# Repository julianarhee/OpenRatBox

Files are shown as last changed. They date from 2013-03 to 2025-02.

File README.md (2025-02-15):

# Open Rat Box
This repository contains part files and instructions for high-throughput behavior rig towers (current and previous designs).

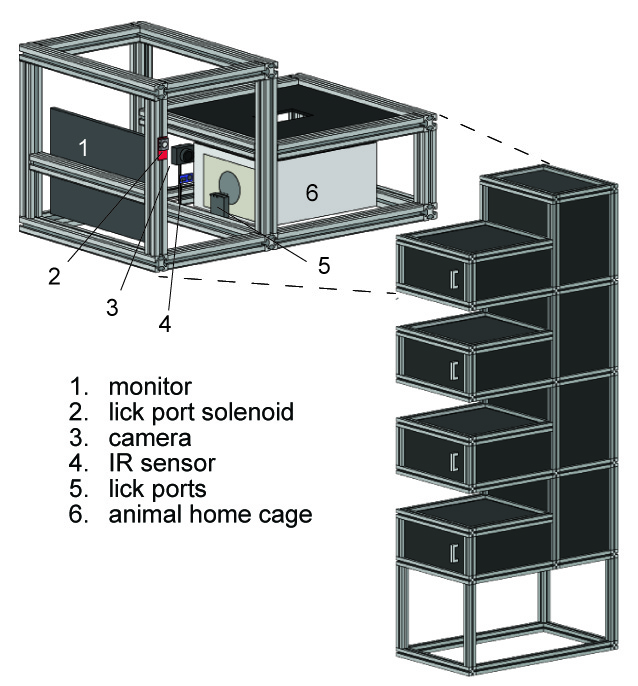
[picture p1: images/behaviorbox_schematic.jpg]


## Components 
- cage: cage info (mounting point dimensions, etc...)
- camera: webcam info
- displays: small computer monitor & optional usb touchscreen display
- frame: 80/20 extrusion bars 
- acrylic panels: structural (walls, ceiling, floor), and useful mounts  
- plumbing: 1/4" ID tubing for connecting water pump to the lick ports (feeding needles attached with luer locks)
- pumps: syringe pumps that can be programmed to deliver set amounts of fluid based on speed, tubing diameter, etc.
- sensors: IR reflector to detect presence/absence of the head poking out of the cage, touch sensors wired to feeding needles (lick ports) to detect lick or no lick

## Instructions
`instructions`: Start here!
- `instructions/behav_rg_special_notes.md`: Contains construction notes and additional tips.
- `instructions/behav_rig_specs_final.xls`: Optional spreadsheet to sort out what size bulk acrylic to buy based on dimensions of custom cut acrylic pieces (disclaimer: might not be fully accurate).

## Design files
`add_ons`: Additional acrylic pieces for the tower.
- `add_ons/cage_hole`: Creates an acrylic hole for the rat's head during training. The `inner_plate` attaches inside the cage and the `outer_plate` mates to it on the outside. Both plates are not necessary if just gluing the plates directly to the cage. Start by drilling or cutting a large hole in the cage, then place the acrylic plate with the (more nicely) laser-cut hold on top to create a smoother opening for the head.
- `add_ons/extrusion_support`: Add these to provide support at the junction connecting two extrusion bars. Use the through holes and M6-slot bolts placed on either side of the connection between the bars.
- `add_ons/power_squid_mount`: Convenient mount to hold up a powerstrip for a given training box. We used a power squid rather than a strip.
- `add_ons/spacers`: For use with repurposed metal frames that hold cages in portable colony racks. These are useful to make the metal rack fit snuggly between the top and bottom panels of the main vestibule.

`displays/usb`: Option mounting piece for attaching a little touchscreen display to control each computer.

`foamboard`: Additional pieces to block out light around the separate front area where the monitor is, in front of the rat and main vestibule (can ignore the foamboard folder in `front_area`)
- `foamboard/rack_top`: captured piece for the top and bottom of the front vestibule that contains the monitor
- `foamboard/front_slim`: Fills the gap above the main vestibule (the "L" shape of the box creates blank space above)
- `foamboard/side_captured`: If not using an acrylic side panel (see `main_vestibule/sides`), can just use a foamboard to close the area on the side.

`front_area`: This is the part of the training box that does not contain the rat cage, but just the monitor, separate from the main vestibule.
- `front_area/monitor_mount`: acrylic panel with through holes for mounting a monitor to the extrusion bar
- `front_area/side_frame`:  Can be used with `side_door` or `side_slotted`. This panel creates a frame whose outer edges are fit into the extrusion rails. It has holes to then attach a door, either via thumbscrew (`side_door`) or fully screwing in at all four courners (`side_slotted`)
- `front_area/side_door`: If using `side_frame`, this is a simple rectangular piece that can be detached/attached with a thumbscrew. Useful for closing off the side, but can be removed (if using oe of the frame pieces) to access wires and such on the monitor-side of the vestibule.
- `front_area/side_slotted`: Screws into `side_frame` with 4 screws, and has a small slotted opening for wires to come through

`main_vestibule`: Where the rat cage is
- `base`: bottom or floor of the vestibule
- `door`: door that attached with hinges and has a handle to make it easy to open/close the box
- `lid`: top of vestibule
- `sides`: sides of vestibule (they should be oriented the same way)
- `front_clear`: `frame` fits into the extrusion rails, and is meant to make the `attachment` window pane removable. The `attachment` panel screws into the `frame` in 4 corners, and also contains slotted holes to allow wiring from the lick ports to come through, out of the front vestibule.

`sensors`: Mounts to hold various sensors
- `head`: If using an IR reflector sensor to detect head presence/absence, holds that phidget sensor in place. Not really critical, as the small PCB can be directly screwed onto the MicroRax frame that sits between the `main_vestibule/front_clear` panel and the rat's cage hole.
- `lick`: 1 or 3 lick ports (clear). Holds the feeding needles that deliver reward, which are also metal (conductive). A small hole should be tapped at the top (M2.5) to hold the lick spout in place, like a set screw. A flat washer can be placed under the screwhead with a wire soldered on in order to create a connection between the lick port and the little touch sensor board outside of the vestibule.
- `phidget_mounts`: A mount to hold the USB-phidget which connects all the different sensor boards (IR reflector, touch sensors for the lick port detection, etc.)

`tower_frame`: All specifications for the custom-cut extrusion bars, and additional notes.

`x_everything`: When in doubt, all the pieces (might not contain everything though). Always use the most recent version.

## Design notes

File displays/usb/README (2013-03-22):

To setup the usb display...

1) install display driver: http://www.displaylink.com/support/mac_downloads.php
2) install touch driver: http://www.touch-base.com/documentation/mimotouchdevice.htm
3) calibrate
4) set as primary display

Notes
------

After proper installation, should have "UPDD Console" and "UPDD Calibrate" programs. Use the Console to choose Display 1 as the touchscreen monitor (primary), then calibrate by clicking correct icon in the Console (use precise pointer to touch the 4 calibration points).

The display driver may not work with 'Standard' rotation of the display. If so, set the rotation to 180, and flip the monitor. Then recalibrate the touch screen.

Additional configuration information: http://www.mimomonitors.com/pages/mac-os-x-install-procedures-for-mimo-710-710-s-720-s-740

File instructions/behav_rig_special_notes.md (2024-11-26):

# Building notes
- Do not build the entire tower out of the anodized extrusion bars first. Start with the base, then build each unit on top of the next. 
- Use the labeled tower diagram to make sure bars are not mixed up (components A, B, C, etc. in `tower_frame/rat_box_assembly.png`). Each component has its own specification, such as which ends are tapped, which are not, etc. 
- Read the whole document (especially "Idiosyncracies for construction"). 
- Laser-cut and prepare all custom modifications for a *single* unit (the bottom unit) first. Only once you are satisfied with the base unit, then can cut more pieces for each unit. 

## Custom components
- All laser-cut pieces
- MicroRax frame & attachment pieces (LED, camera, sensors) for all components near the head and lickport area inside the main vestibule
- wiring: LEDs (IR for camera, etc.), phidget sensors (IR reflective sensor for head-detection & to lick spouts)
- tubing: helpful to have an extra, long piece of tubing to attach to the lick ports when flushing the system for cleaning. Supergluing a small rubber black O-ring to the cross-section of tube will help create a snug fit onto the rounded lickport spout

## Modifications related to laser-cut parts

### Pieces that need tapped holes
- `lickHolder`: needs 2 tapped holes for M2.5 screws
- `frontPanelFrame` (clear):  needs 4 tapped holes for M3 screws (tap M3x0.50)
-side door frame (black, captured):  needs 1 tapped hole at the top if using thumb-screw for panel

### Pieces with added holes
- `monitorMount` ("big"): make spacing of 4 through holes match whatever mount the monitor needs\
- `touch_sensor_panel` (for `phidget_mounts`): drill little holes above each sensor board for zip-ties to hold soldered wires straight up (prevents bending)

### Bulk acrylic order adjustments
- Make sure large, bulk pieces fit the laserbed, for ex., cut in half (18.5" and 17.5", not 36") to fit
- `phidget_mount` and `touch_sensor_panel` (clear): cut with 1/8" acrylic (not 1/4")
- might need more black 1/4" for `side_door_frame` depending on size (capture inside extrusion rivets)
- `cage_head_thruHole` (for gluing to front of rat cage where head pokes out): use 1/8" rather than 1/4" acrylic for spacing

## Idiosyncracies for construction:
1. If using spring-loaded spacer pieces (which can also be used for optional air flow) should be installed *before* putting in the lid/bottom panels. These pieces go on the underside of the top frame of the vestibule, so it is easier to screw them on (springs, screws, etc.) when the panel is upside down than when installed.
2. If using repurposed metal brackets from the colony cage system, for a snug fit, helpful to add: one 1/4" acyrlic spacer set on bottom (use M5x20s), and two stacked 1/4" spacers attached to top/lid piece (use M5x25s).
3. All vertically-oriented extrusion pieces should be screwed in to its lower horizontal piece before stacking the next unit on top of rack. Otherwise, you cannot access the end-fastener at the bottom of the vertical piece once it is in place.
4. `main_vestibule/lid/Lid` and `base/Bottom`: These are the black acrylic panels that are fitted into the extrusion frames forming the top (lid) and floor (bottom) of the main vestibule holding the plastic rat cages. The etched text (in the laser cut pattern) should be facing up. And, "insert this side first" means that end goes toward the monitor first.
5. `main_vestibule/sides/sidePanel_final_rot`: Side panels for main vestibule should face the same direction, so the text should be facing leftward, if facing the monitor.
6. `main_vestibule/front_clear/frame` and `front_clear/attachment` pieces  are clear acrylic panels that should be screwed together before inserting (i.e., don't just put the frame in alone while building up the extrusion pieces around it without screwing on the attachment piece, too)

### Helpful ordering of main vestibule:  
(a) Get bottom extrusion frame (3 pieces, sides and front), but without the front piece connected yet, and slide in the acrylic bottom panel. The spacers & metal cage frame should be screwed in already (Note 2 above).
(b) Approximately align the top horizontal extrusion pieces (into which the lid panel will fit) with the horizontal extrusion piece that is  resting above the clear acrylic front panel/attachment
(c) Then, slide in the side panels.
(d) Separately, build up the door (bottom and side extrusion bars, but without the top bar connected). Connect this partial door to the extrusions making up the bottom of the vestibule. Make sure that the side acrylic panels are fitting into the vertical extrusion bars of the door as you screw the door into the end fasteners on the bottom frame's extrusion bars.
(e) With the top extrusion bar of the door still off, slide in top acrylic panel for the lid. Then, slide in the extrusion bar that will connect the edge closest to the door of the top panel and the top of the door.

### Some more notes:
- For securing the top/bottom acrylic panels, manuever the pieces so that for each panel, 3 edges (two sides and the edge closer to the monitor) are resting on the extrusions that make up the sides and front (closest to monitor) of the vestibule. Place the 4 panel pieces (sides, top, bottom) in the approximate places, and don't tighten until things are well in place. Make sure all panels are securely backed all the way in (toward the monitor), i.e., the acrylic panels should nestle fully into the rails of the extrusion bars.
- Make sure clear acrylic front panel attachment is screwed onto the front panel frame when inserting into extrusions during building (extrusions on top of the frame were sitting too low, so the front panel attachment did not fit.  had to shave off a little bit off the top of the attachment piece)\
- Add support extrusions to bottom carriage to provide extra support across the longer axis (rigs may bend forward otherwise). Use 2 M6 T-slot nuts, with acrylic piece, same length as 4 main carriage extrusion pieces.

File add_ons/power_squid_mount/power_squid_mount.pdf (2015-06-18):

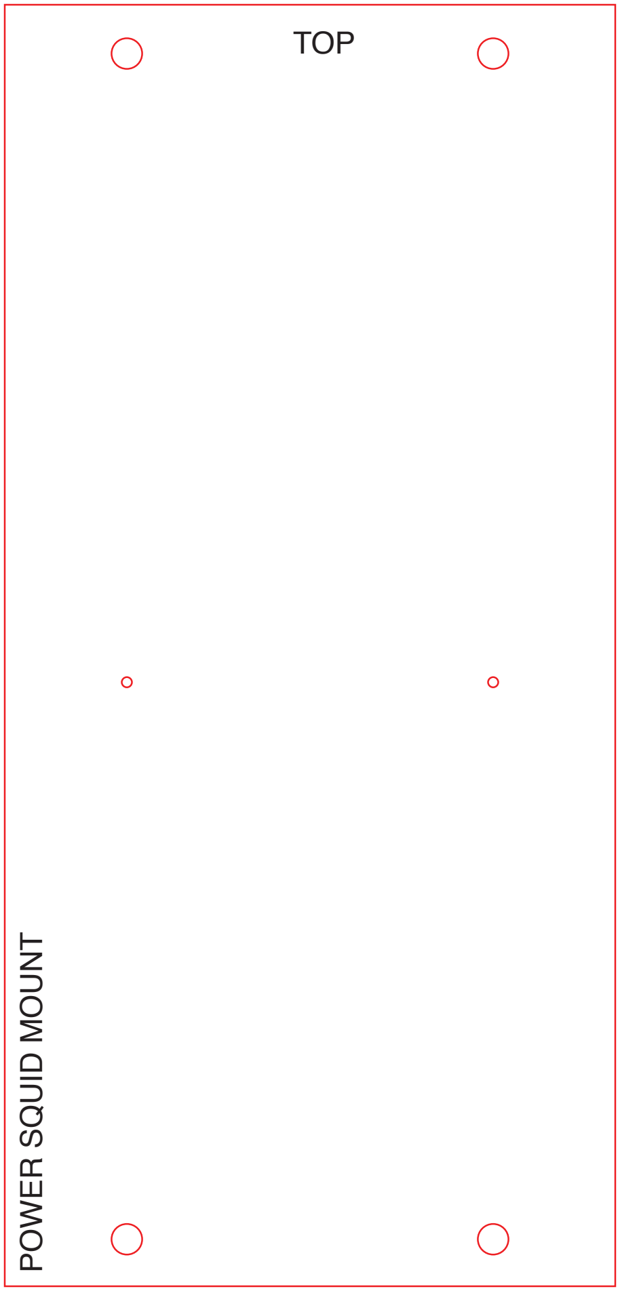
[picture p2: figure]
TOP; POWER SQUID MOUNT

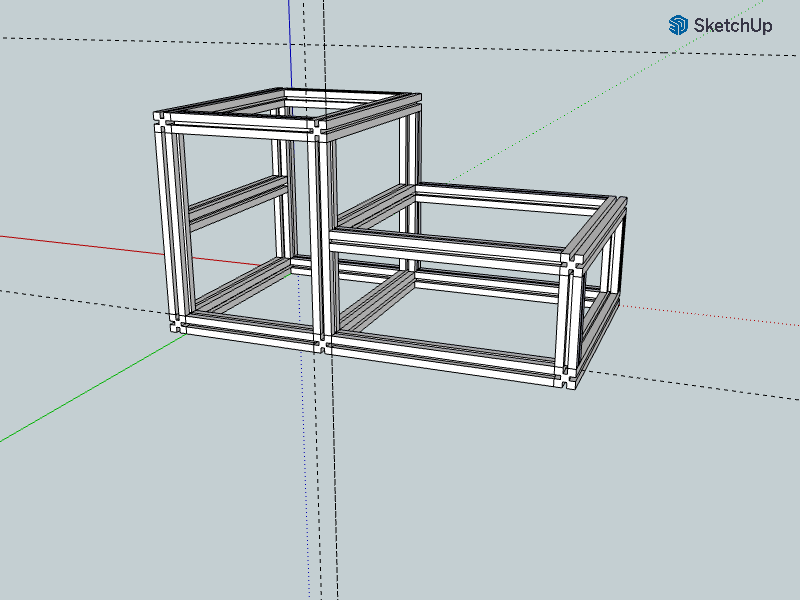
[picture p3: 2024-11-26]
tower_frame/rat_box.png

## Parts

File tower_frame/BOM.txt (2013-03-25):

All pieces below: 4040-lite, black anodized

Per Box (4 per tower):

4x  A	(525mm, end fastener access holes, both sides, both axes)
	40-4040-LITE X 525MM
	80/20 Metric Extrusion
	Black Anodized.With 40-7050 Style MA in R&S Left End and 40-7050 in R&S Right End.
	
2x  B	(210mm, both sides tapped for end fasteners)
	40-4040-LITE X 210MM
	80/20 Metric Extrusion
	Black Anodized. With 40-7059 Both Ends

4x  C	(450mm, tapped on one side for e.f., milled on other for anchors)
	40-4040-LITE X 450MM
	80/20 Metric Extrusion
	Black Anodized. With 40-7059 One End,& 40-7044 @ A,C Opposite End.

2x  D	(445mm, milled for anchor fasteners on both sides, same axis -- e.g. A&C)
	40-4040-LITE X 445MM
	80/20 Metric Extrusion
	Black Anodized. With 40-7044 @ A,C Both Ends.

2x  E 	(300mm, tapped on both sides for e.f.)
	40-4040-LITE X 300MM
	80/20 Metric Extrusion
	Black Anodized. With 40-7059 Both Ends.

4x  F 	(385mm, tapped on one side, milled for a.f. on other)
	40-4040-LITE X 385MM
	80/20 Metric Extrusion
	Black Anodized. With 40-7059 One End & 40-7044 @ A,C Opposite End.

Capping off the top (1 per tower)

2x A
2x E

Bottom carriage (1 per tower)

6x  G   (280mm, tapped on one side, milled for a.f. on other)
	40-4040-LITE X 280MM
	80/20 Metric Extrusion
	Black Anodized. With 40-7059 One End & 40-7044 @ A,C Opposite End.

2x  H 	(790mm, tapped on both sides for end fastener)
	40-4040-LITE X 790MM
	80/20 Metric Extrusion
	Black Anodized. With 40-7059 both Ends.

+2x A

Full tower:

A: (4*4) + 2 + 2 = 20
B: (2*4) = 8
C: (4*4) = 16
D: (2*4) = 8
E: (2*4) + 2 = 10
F: (4*4) = 16
G: 6
H: 2

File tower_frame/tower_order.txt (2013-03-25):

2 Towers:

A: ((4*4) + 2 + 2) * 2 = 40
B: (2*4) * 2 = 16
C: (4*4) * 2 = 32
D: (2*4) * 2 = 16
E: ((2*4) + 2) * 2 = 20
F: (4*4) * 2 = 32
G: 6 * 2 = 12
H: 2 * 2 = 4

(less extra from past orders + 2 for safety margin)
A: 40 - 12 + 2 = 30
B: 16 + 2 = 18
C: 32 + 2 = 34
D: 16 + 2 = 18
E: 20 - 12 + 2 = 10
F: 32 + 2 = 34
G: 12 + 2 = 14
H: 4 + 2 = 6

30x  A	(525mm, end fastener access holes, both sides, both axes)
	40-4040-LITE X 525MM
	80/20 Metric Extrusion
	Black Anodized.With 40-7050 Style MA in R&S Left End and 40-7050 in R&S Right End.	
18x  B	(210mm, both sides tapped for end fasteners)
	40-4040-LITE X 210MM
	80/20 Metric Extrusion
	Black Anodized. With 40-7059 Both Ends

34x  C	(450mm, tapped on one side for e.f., milled on other for anchors)
	40-4040-LITE X 450MM
	80/20 Metric Extrusion
	Black Anodized. With 40-7059 One End,& 40-7044 @ A,C Opposite End.

18x  D	(445mm, milled for anchor fasteners on both sides, same axis -- e.g. A&C)
	40-4040-LITE X 445MM
	80/20 Metric Extrusion
	Black Anodized. With 40-7044 @ A,C Both Ends.

10x  E 	(300mm, tapped on both sides for e.f.)
	40-4040-LITE X 300MM
	80/20 Metric Extrusion
	Black Anodized. With 40-7059 Both Ends.

34x  F 	(385mm, tapped on one side, milled for a.f. on other)
	40-4040-LITE X 385MM
	80/20 Metric Extrusion
	Black Anodized. With 40-7059 One End & 40-7044 @ A,C Opposite End.

14x  G   (280mm, tapped on one side, milled for a.f. on other)
	40-4040-LITE X 280MM
	80/20 Metric Extrusion
	Black Anodized. With 40-7059 One End & 40-7044 @ A,C Opposite End.

6x  H 	(790mm, tapped on both sides for end fastener)
	40-4040-LITE X 790MM
	80/20 Metric Extrusion
	Black Anodized. With 40-7059 both Ends.

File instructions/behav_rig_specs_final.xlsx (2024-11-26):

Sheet: acrylic piece sizes to order
Piece | File Name | Material | Width | Height | Bulk Piece Assignments: |  |  | laserbed | base or lid | door |  | sensor base (2) |  | TOTAL:
Base | Bottom_v6 | Acrylic (1/4") | 18 | 18.5 |  | c | b1 | W: | 18.5 | 17.25 |  | 8 |  | 35.75
Lid | Lid_v11 | Acrylic (1/4") | 18 | 18.5 |  | c | b1 | H: | 18 | 8.825 |  | 1 |  | 9.825
Door | door_v6 | Acrylic (1/4") | 17.25 | 8.825 |  | c | b3
door hinge | doorHinge_v8 | Acrylic (1/4") | 4 | 8.24 |  | c | b3 | laserbed | lid | spacers | monitor mount | door hinge | 1 cage head hole | 3 sensor bases | 9 lick holders | TOTAL:
lick spout holder | lickHolder_v4 | Acrylic (1/4") | 0.663 | 1.5 |  | c | b3 | W: | 18.5 | 9 | 8.5 | 8.25 | 5 | 3 | 9 | 36 | 35.75 | 35.5 | 35.5
Monitor mount | monitorMount_v3 | Acrylic (1/4") | 8.5 | 6 |  | c | b3 | H: | 18 | 15 | 6 | 4 | 8 | 8 | 1.5 | 18 | 16.5 | 18
sensor base | sensorBase_v? | Acrylic (1/4") | 8?? | 1 | *check, bec IR distance is 10cm, or approx 4in. | c | b3
side panel | sidePanel_v2 | Acrylic (1/4") | 18.5 | 8.852 | (x2) | c | b1 |  | 8.5 | 27.5
spacer (air) | spoutSpacer_v1_airOnly1c | Acrylic (1/4") | 5 | 4.5 | (x3) | c | b2
spacer (H2O) | spoutSpacer_v1_H2Oonly | Acrylic (1/4") | 5 | 4.5 | (x3) | c | b2
(cage head hole pieces) |  | Acrylic? | 8 | 5 | (x2) |  | b3 | Estimated Bulk Acrylic Pieces to Order:
 |  |  |  |  |  |  |  | b1 | 18x18.5 | 3
front panel frame | frontPanelFrame_v2 | clear Acrylic | 18.4 | 8.852 | *inner area = 16.5x6.85 |  |  | b2 | 9x15 | 1
front panel | frontPanelAttachment_v2 | clear Acrylic | 17.37 | 8 |  |  |  | b3 | 18x19 | 1
phidget sensor holder | x | clear Acrylic | 7.5 | 4.5
phidget holder | x | clear Acrylic | 7.5 | 3.5 |  |  |  |  |  |  |  | 25
 |  |  |  |  |  |  |  | c1 | 9x36 | 1
monitor side cover (removable) | x | Foam board | 15 | 18 | f3
monitor side cover (trapped) | use monitorFloor_v2 (w/o slots) | Foam board | 18.5 | 12.5 | f2
Monitor area base | monitorFloor_v2 | Foam board | 18.5 | 12.5 | f2 |  |  | 36 | 17 |  |  | 6
back monitor cover top | use sidePanel_v2 (w/o corners) | Foam board | 18.5 | 8.852 | f1 |  |  | 15 | 25.5
back monitor cover (bottom) | use sidePanel_v2 (add slots) | Foam board | 18.5 | 8.852 | f1
front cover panel | x | Foam board | 18.5 | 6.5, 6.25 | f4 |  |  | Estimated Bulk Acrylic Pieces to Order:
top cover panel | x | Foam board | 18.5 | 13 | f2 |  |  | f1 | 18x18.5 | 1
 |  |  |  |  |  |  |  | f2 | 18x13 | 3 | 17
 |  |  |  |  |  |  |  | f3 | 18x15 | 1
 |  |  |  |  |  |  |  | f4 | 18.5x7 | 1
 |  |  |  | 33.5 | 13 | 37
 |  |  |  | 31.5 | 25.5

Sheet: accessory pieces
MAIN VESTIBULE:
1. LID AND BASE
Set Panel Holder (M8x16mm) | 8x | (top and bottom panels each req. 4)
1a. Base piece
M5x20 w/ M5 nuts + flat/lock washers | 6x | (attach frame and 1 set of spout spacers to bottom panel)
M5x10 w/ M5 nuts + lock washers | 6x | (to connect metal frame to L-bracket -- aligns elongated hole of L-bracket)
L-brackets (M5 hole & elongated hole) | 12x | (for spout spacers)
1b. Lid piece
M5x25 w/ M5 nuts + flat washers | 6x | (for 2 sets of spout spacers to lid)
(cone springs) | 2x | (come with old rack)
(half-threaded screws for plastic vents) | 6x | (come with old rack)
(pastic vents) | 2x | (come with old rack)
M4x10 (flat, phillips head -- flush with frame) | 4x | (for mac mini cuff -- comes with mac cuff)
Mac Mini cuff | 1x
2. Door
M6x16, + M6 nut; flat-lock washers | 2x | (for attaching door_hinge panel to hinge)
Hinge | 1x | (comes with 4 M6 roll-in T-slot nuts & M6 screws: use 2 to attach hinge to extrusion, \
 |  |  | other 2 go on opposite extrusion bar, to attach slim piece for dead-bolt)
M6x25, + M6 nut; flat--flat-lock washers | 2x | (for attaching door_main to door_hinge panel)
Dead bolt | 1x
M5x12, + M5 nut; flat-lock washers | 4x | (for attaching dead-bolt to acrylic door_main piece)
Door handle | 1x
M4x10, + flat washers | 2x
(M6 w. roll-in T-slot nut) | 2x | (for attaching hinge to Extrusion; comes with Hinge)
(M6 w. roll-in T-slot nut (for dead bolt) | 2x | (for dead-bolt latch to attach to extrusion; comes with Hinge)
3. Front clear panel piece
M3x10 | 4x | (front clear panel -- screw into tapped holes on front_panel_frame piece, captured)
MONITOR AREA:
1. Monitor
M4x20 (or M4x25) screws | 4x | (for screwing back of monitor to monitor_mount)
Large flat washers (M4) | 4x
M6 w/ roll-in T-slot nut | 2x | (for attaching monitor_mount to extrusion bar)
2. Side door
M6 thumb screw | 1x | (for screwing side door onto side_door_frame, captured -- tapped hole)
(black vinyl cover, as a "window curtain"?)
... door should just be red acrylic?? (1/8")
Wheels
M6(or M8) w/ roll-in T-slot nut | 12x
wheels | 4x
SENSORS
1. Phidget / attachments
M6 w. roll-in T-slot nut | 4x | (attach phidget and touch-sensor mounts)
M4x16 w/ (rectangular) drop-in nut (+ M4 flat washers, for pumps) | 2x; 2-4x | (Startech network adaptor; 1-2 pumps) -- roll-in spring loaded ones might be better, esp for pumps…
Touch Sensors | 1-3x
IR Reflective sensor (min 10 cm) | 1x
USB camera (Newegg) | 1x
red LED light bar | 1x | (+ power source for 4 LEDs -- per tower)
Reward spouts | 1-3x
M2.5 x6mm (with washers, flat and lock) | 2-6x | (for each spout)
wire w/ banana clips & U-hooks | 3x | (to connect each spout to phidget sensor)
(sheet metal piece) | 1-3x | (for each spout)
2. MicroRax Parts
320 cm bar (350 cm might be fine, too) | 1x
M3x6 (connects 90deg bracket to L-bracket & microrax frame) | 2x | <-- if get correct length long-bar, might not need
M3x5 (reg head) for all else
M3x5 low-head -- for 90deg bracket between 2cm & 4cm piece (holds lick-spout piece) | 2x, w/ lock washers
M2.5x6 (for holding spout) | 2x
M3x8 (for holding lick-spout acrylic piece to frame) | 2x
cage-frame mount bar, 160 cm
head-sensor bar, 140 cm
spacer bar (attaches to truss piece), 4cm (or 5cm)
camera stand, 6cm (attaches to cage-frame mount bar)
lick-spout bar, 4cm
OLD microrax arrangement for sensors:
200mm bar | 2x | MicroRax frame
300mm bar | 2x | MicroRax frame
M3 (like MicroRax kit screws and T-slot/reg nuts) | (22x, nut bar; 4x, reg nut) | (to make MicroRax frame)
M3(x16) with washers | min 2x | (for MicroRax frame to base)
2mm bar pieces
4mm bar pieces
flat L-brackets (to connect frame pieces) | 4x + however many for add-on pieces
short 90-deg brackets + screws/nuts | ? X | (plus, 1 M3x8 (?) for connecting 90-deg bracket + (washer) + nut-plate on frame)

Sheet: finalized pieces
Piece | File Name | Material | Width | Height | Qty/setup: | Qty/rack: | Raw Piece: | Price | laserbed | base or lid | door |  | sensor base (2) |  | TOTAL:
MAIN_VESTIBULE
Base | Bottom_v5_imported_rot_text_dxf.dxf | black Acrylic (1/4") | 18 | 18.5 | 1x | 4x | B1, 1x |  | W: | 18.5 | 17.25 |  | 8 |  | 35.75
Lid | Lid_v15_imported_rot_text_dxf.dxf | black Acrylic (1/4") | 18 | 18.5 | 1x | 4x | B1, 1x |  | H: | 18 | 8.825 |  | 1 |  | 9.825
Door (main) | door_final_text.dxf | black Acrylic (1/4") | 17.25 | 8.825 | 1x | 4x | B3
Door (hinge) | doorHinge_final_rot.dxf | black Acrylic (1/4") | 4 | 8.24 | 1x | 4x | B4*, use inner area -- makes 2x per B4 piece) |  | laserbed | lid | spacers | monitor mount | door hinge | 1 cage head hole | 3 sensor bases | 9 lick holders |  | TOTAL:
Front Panel (attachment) | frontPanelAttachment_final_rot.dxf | clear Acrylic (1/4") | 17.37 | 8 | 1x | 4x | C1a (17.5"x9")
Front Panel Frame (tapped, M3, x4) | frontPanelFrame_final_rot.dxf | clear Acrylic (1/4") | 18.4 | 8.852 | 1x | 4x | C1b (18.5"x9"), *inner area = 16.5x6.85
sides (2x) | sidePanel_final_rot_text.dxf | black Acrylic (1/4") | 18.5 | 8.852 | 2x | 8x | B1, 1x
 |  |  | (tot: 18.5 x 18")
FRONT VESTIBULE (Monitor) | [sideDoorAttachment_v4 is the shorter panel -- use this]
side door (attachment) (M6 thumb or 4 M3 tapped) | sideDoorAttachment_v5_imported_dxf.dxf | black Acrylic (1/8") | 11.5 | *15 (short version) | 1x | 4x | r1* (12x16), 1x -- GET IN CLEAR-RED ACRYLIC, 1/8" if possible
side door (frame) (tapped, M6, x1) | sideDoorFrame_v4_imported_dxf.dxf | black Acrylic (1/4") | 12.5 | 16.25 | 2x | 8x | B4* (12.5" x 16.5"), *inner area = 10x13"
Monitor mount | monitorMount_final_rot.dxf | black Acrylic (1/4") | 8.5 | 6 | 1x | 4x | **use B2 sizing -- makes 2x per B2 piece |  | W: | 18.5 | 9 | 8.5 | 8.25 | 5 | 3 | 9 |  | 36 | 35.75 | 35.5 | 35.5
(monitor mount, "big") | (curr: monitorMount_v3_big.dxf -- spacing off) | black Acrylic (1/4") | 8.5 | 6 | (1x) | (4x) | " " |  | H: | 18 | 15 | 6 | 4 | 8 | 8 | 1.5 |  | 18 | 16.5 | 18
**side_door_slotted (4 M3 tapped) | (curr: side_door_slotted_v1 -- make slot smaller) | black Acrylic (1/8") | 11.5 | 15 | 1x | 4x | b1*, 1x
FOAMBOARD PIECES
front slim (captured) | frontSlimCaptured_v2_imported_rot.dxf | Foam board | 18 | 6 | 1x | 4x
*monitor floor | (use same piece as rackTop) | Foam board | 18.5 | 12.5 | 1x | 4x
*rack top | rackTop_final_imp.dxf | Foam board | 18.5 | 12.5 | n/a | 1x
ADD-ONS
(spacer, air only) | spoutSpacer_airOnly_final_imported_rot_text.dxf | black Acrylic (1/4") | 5 | 4.5 | (3x) | n/a | n/a
(spacer, H2O) | spoutSpacer_H2Oonly_final_imported_text.dxf | black Acrylic (1/4") | 5 | 4.5 | (3x) | n/a | n/a |  |  | 8.5 | 27.5
spacers (all, for 9"x15" piece): | spoutspacers_all_imported.dxf | black Acrylic (1/4") | 9 | 15 | 1x | 4x | B2, 1x
cage head hole pieces - inner (tapped, M3/4?, x4) | cage_head_tapHole_imported_dxf.dxf | black Acrylic (1/4") | 8 | 5 | 1x | (4x) | B4*, use inner area -- makes 3x per B4 piece
cage head hole pieces - outer (thru) | cage_head_thruHole_imported_dxf.dxf | black Acrylic (1/8") | 8 | 5 | 1x | 4x | b1* (2 per b1 piece)
extrusion supports | extrusionSupport_imported_dxf.dxf | black Acrylic (1/4") | 1.5 | 4 | n/a | 4x | (can use scrap pieces)
 |  |  |  |  |  |  |  |  | B1 | 18x18.5 | 3 | .=>
touch sensor holder | touch_sensor_panel.pdf | clear Acrylic (1/8") | 7.5 | 4.5 | 1x | 4x | ** |  | B2 | 9x17.5 | 1
phidget holder | touch_sensor_panel.pdf | clear Acrylic (1/8") | 7.5 | 3.5 | 1x | 4x | ** |  | B3 | 18x19 | 1 | NO
lick spout holder (tapped, M2.5, x2) | lickHolder_v6_imported_dxf (1).dxf | clear Acrylic (1/4") | 1.6 | 1 | 1x - 3x | 4x - 12x | C1b (make out of inner area of front frame) |  | B4 (new) | 12.5" x 16.5" | 2
[head sensor holder ] | mag_head_sensor.pdf | black Acrylic (1/4") | 1.25 | 1.25 | 1x | 4x+ | (scrap pieces, not part of new design) |  |  |  |  |  |  | Per Setup | Per Tower
 |  | black Acrylic (1/8") | 1.25 | 1.25 |  |  | " " |  | B2' | 9x15 | 1 | (2 monitor_mounts) |  | 0.5x | 2x
 |  |  |  |  |  |  |  |  | **adjust to 9" x 17.5" -- use B2to make door (dims 17.25x8.825), getting rid of "B3" piece, plus giving extra 2.5" pieces for scraps
 |  |  |  |  |  |  |  |  | B2 adjusted | 9x17.5 | 1 | (1 door) |  | 1x | 1x
RAW ACRYLIC TO ORDER:
black 1/4" acrylic (18.5"x18") |  |  |  |  |  |  |  |  | C1 | 9x36 | 1
black 1/4" acrylic (19"x18") |  |  |  |  |  |  |  |  | **splt C1 original to: |  | (a) 9" x 17.5" |  | "C1" (=C1a) | 1x | 4x
black 1/4" acrylic (15"x9") |  |  |  |  |  |  |  |  |  |  | (b) 9" x 18.5" |  | "C2" (=C1b) | 1x | 4x
clear 1/4" acrylic (17.5"x9") |  |  |  |  |  |  |  |  | b1 | 12" x 16" | 1 |  | "b1" | 1x | 4x
clear 1/4" acrylic (18.5"x9") |  |  |  |  |  |  |  |  | c1 | (have)
black 1/8" acrylic (W" x H")
clear 1/8" acrylic (W" x H")
black foamboard |  |  |  |  |  |  | RAW ID: | DIM: | PIECE | PER SETUP | PER TOWER | Total: |  | 2 TOWERS: | Already Have: | Need: | NEW ORDER (04.10.2013) |  | *needed amount + 4 extra of each piece (except black 1/8")
black vinyl |  |  |  |  |  |  | B1 | black 1/4" acrylic (19"x18") | "B1" | 3x | 12x | 12 |  | 24 | -28 | 0 | 4
 |  |  |  |  |  |  | B2 | black 1/4" acrylic (17.5"x9") | "B2" | 2x | 8x+2x(B2') | 10 |  | 20 | -8 | 12 | 16 | *changed | [for 8 doors, 8 monitor mounts]
 |  |  |  |  |  |  | B4 | black 1/4" acrylic (12.5"x16.5") | "B4" | 2x | 8x | 8 |  | 16 | 0 | 16 | 20 (sheet makes 24) | *new | [for 16 side_door_frames]
**03.11.2013 notes: |  |  |  |  |  |  | C1 | clear 1/4" acrylic (17.5"x9") | C1 | 1x | 4x | 4 |  | 9 | -9 |  | 4
(1). Change CLEAR acrlyic general dimensions (to fit laser bed) -- also, remove "phidget sensor mount" pieces |  |  |  |  |  |  | C2 | clear 1/4" acrylic (18.5"x9") | C2 | 1x | 4x | 4 |  | 9 | -9 |  | 4
(2). Add 1/8" acrylic pieces -- phidget sensor mounts (both--phidget mount, and lick-sensor mount)
(3). Remove monitor-back covers -- these will just be vynl pieces (add this!), along witih magnetic strips OR just gaffer's tape |  |  |  |  |  |  | b1 | black 1/8" acrylic (12"x15") | b1 | 1x | 4x | 4 |  | 8 | -7 | 9 | 9 | [1 more, plus 8 extra, in case replaced]
(4). Fix "file names" for each piece! |  |  |  |  |  |  | r1 | clear-red 1/8" acrylic (12"x15") | "r1" | " " | " " | " " |  | " " | 0 | 8 | 20 | *new [get 8, OR get 16, if replace all]
(5). Mark "special instructions" if really important, and also, mark which accessory-pieces go with it… (see tab)
 |  |  |  |  |  |  |  | clear 1/8" acrylic | c1 | (have) |  | 36 x 8 ft | 24 pieces | 48 | 4 setups
*(6). Make (new) "raw" pieces that include several parts in one acrylic piece-to-order |  |  |  |  |  |  |  |  |  |  |  | 48" | 48 x 96 | 60 | 4 setups
(for ex., "acrylic_b3"; include "extrusion support" piece, dwg/dxf) |  |  |  |  |  |  |  |  |  |  |  |  |  | 36 | 3 setups

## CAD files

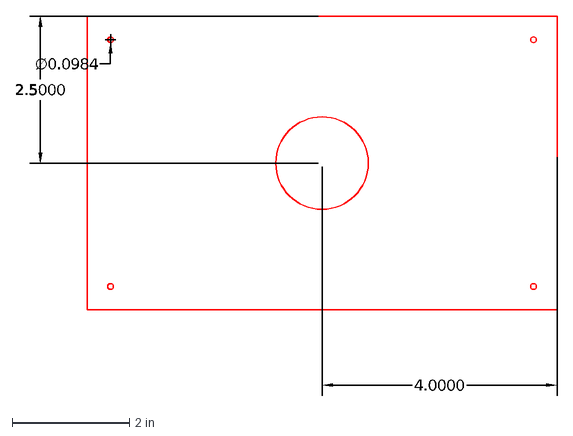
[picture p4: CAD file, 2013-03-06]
add_ons/cage_hole/inner_plate/cage_head_tapHole.dxf
4.0000
2.5000
∅0.0984

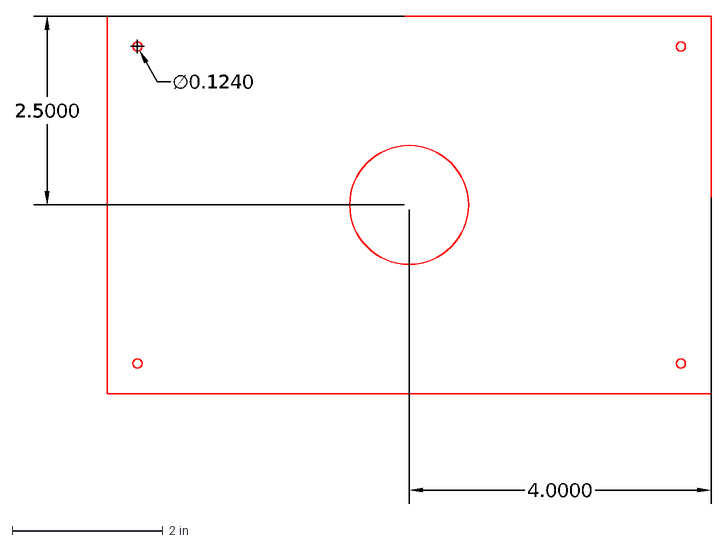
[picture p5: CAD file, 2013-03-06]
add_ons/cage_hole/outer_plate/cage_head_thruHole.dxf
4.0000
2.5000
∅0.1240

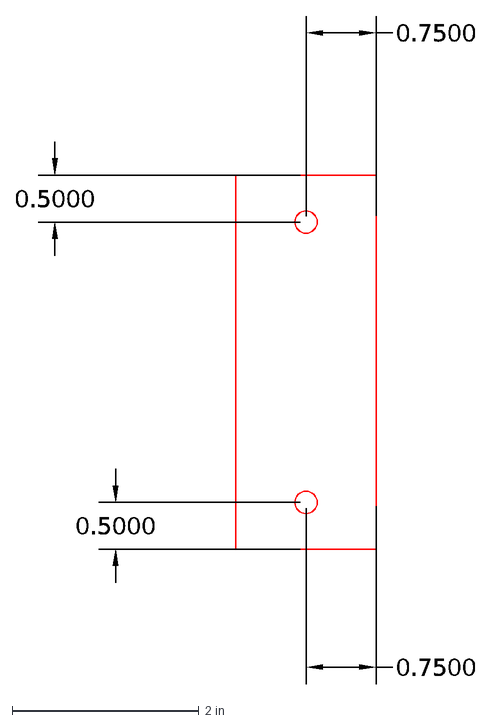
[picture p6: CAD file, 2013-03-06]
add_ons/extrusion_support/extrusionSupport.dxf
0.7500
0.5000

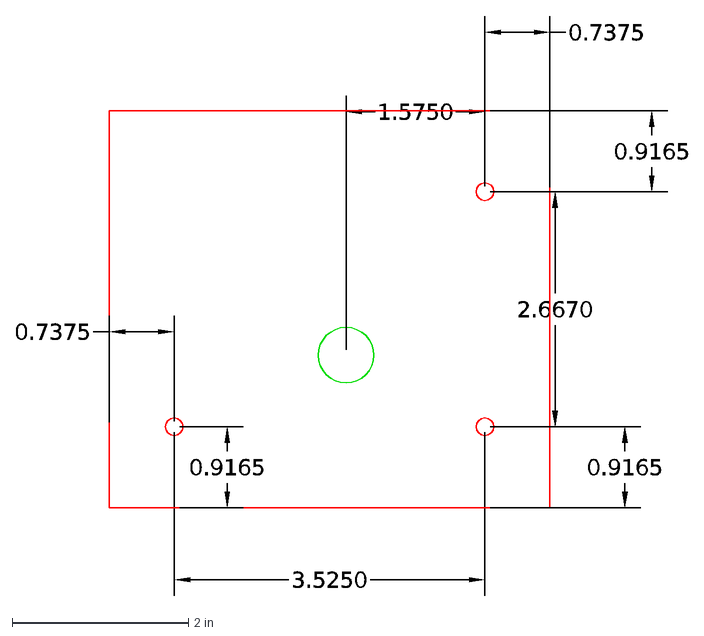
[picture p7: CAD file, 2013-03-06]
add_ons/spacers/singles/spoutSpacer_H2Oonly_final.dxf
2.6670
1.5750
3.5250
0.9165
0.7375

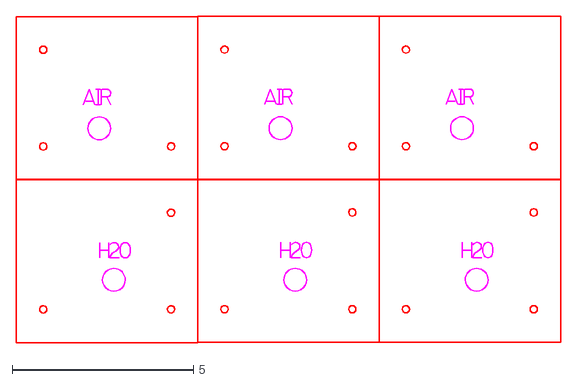
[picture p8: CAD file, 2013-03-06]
add_ons/spacers/spoutspacers_all_imported.dxf
15.0 x 9.00

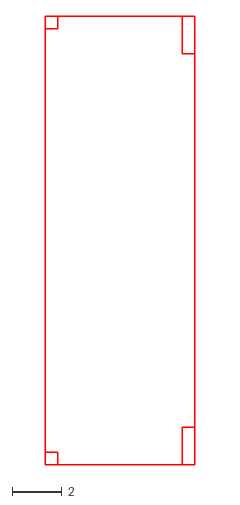
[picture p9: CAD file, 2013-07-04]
foamboard/front_slim/frontSlimCaptured_v4_imported_rot_dxf.dxf
6.00 x 18.0

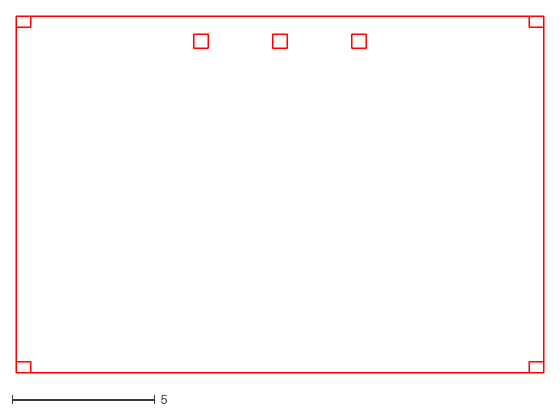
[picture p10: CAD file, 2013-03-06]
foamboard/monitor_floor/monitorFloor_imported_rot_dxf.dxf
18.5 x 12.5

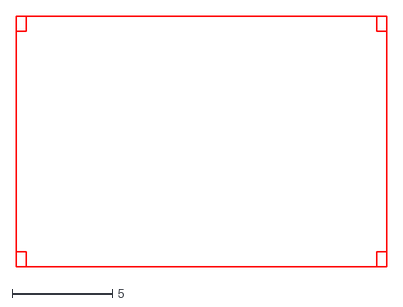
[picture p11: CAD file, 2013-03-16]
foamboard/rack_top/rackTop_final_imported_rot.dxf
18.5 x 12.5

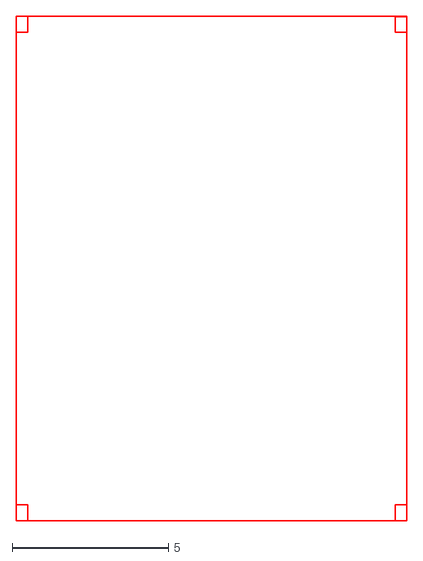
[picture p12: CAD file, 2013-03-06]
foamboard/side_captured/sideCaptured_final_imp.dxf
12.5 x 16.1

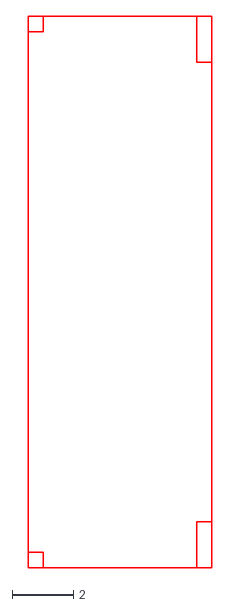
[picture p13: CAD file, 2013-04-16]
front_area/foamboard/front_slim/frontSlimCaptured_v4_imported_rot_dxf.dxf
6.00 x 18.0

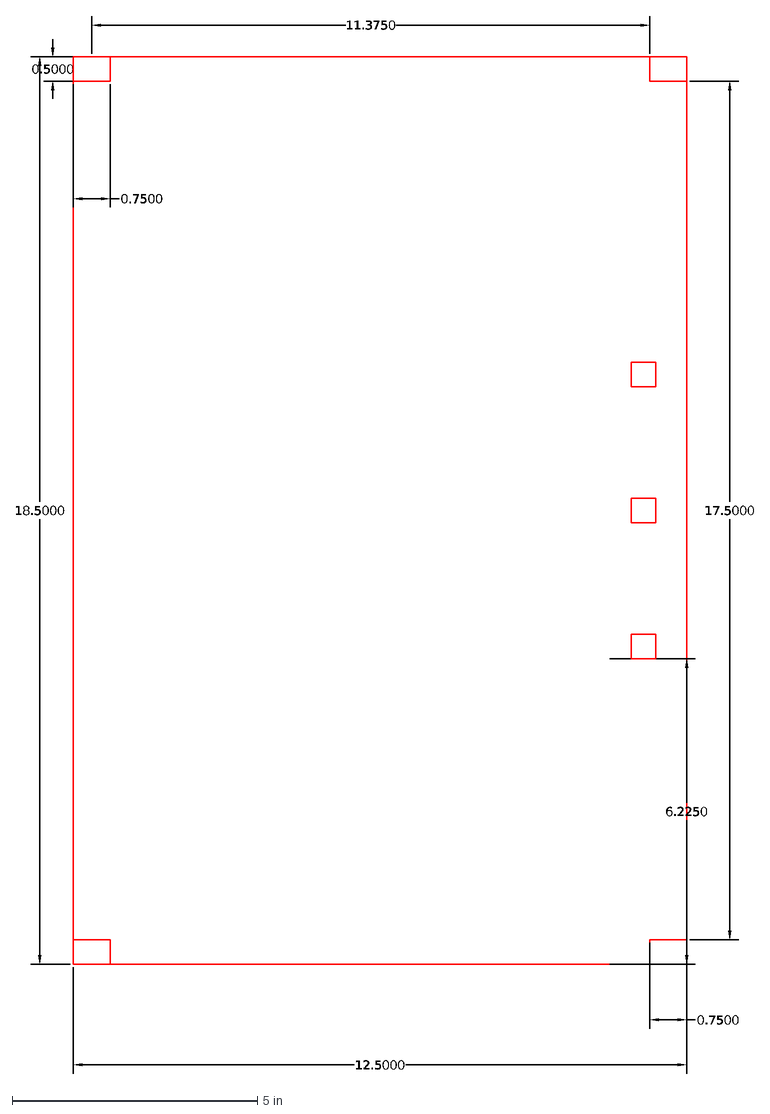
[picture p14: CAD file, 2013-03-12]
front_area/foamboard/monitor_floor/monitorFloor_v4.dxf
11.3750
17.5000
6.2250
0.5000
12.5000
18.5000
0.7500

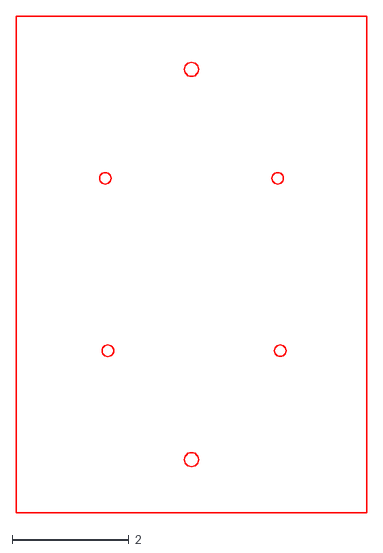
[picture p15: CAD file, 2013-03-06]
front_area/monitor_mount/small/regular/monitorMount_final_rot.dxf
6.00 x 8.50

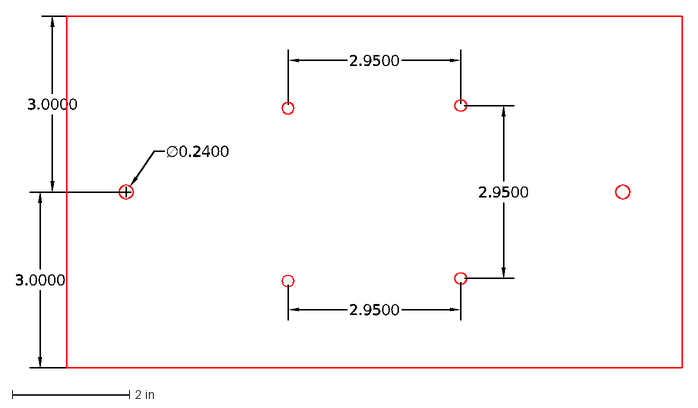
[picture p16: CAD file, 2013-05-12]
front_area/monitor_mount/small/wide/monitorMount_small_extended.dxf
∅0.2400
3.0000
2.9500

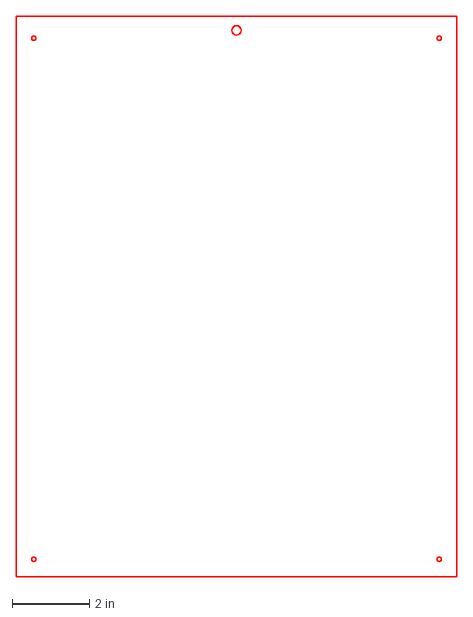
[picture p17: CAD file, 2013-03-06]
front_area/side_attachment/sideDoorAttachment_v3.dxf
11.4 x 14.5 in

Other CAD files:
front_area/monitor_mount/big/monitorMount_new_v1.dwg
front_area/side_door/side_window/side_window_v1_imported_dxf.dxf
add_ons/cage_hole/inner_plate/cage_head_tapHole.dwg
add_ons/cage_hole/inner_plate/cage_head_tapHole_imported_dxf.dxf
add_ons/cage_hole/outer_plate/cage_head_thruHole.dwg
add_ons/cage_hole/outer_plate/cage_head_thruHole_imported_dxf.dxf
add_ons/extrusion_support/extrusionSupport.dwg
add_ons/extrusion_support/extrusionSupport_imported_dxf.dxf
add_ons/spacers/singles/spoutSpacer_H2Oonly_final.dwg
add_ons/spacers/singles/spoutSpacer_H2Oonly_final_imported_text.dxf
add_ons/spacers/singles/spoutSpacer_airOnly_final.dwg
add_ons/spacers/singles/spoutSpacer_airOnly_final.dxf
add_ons/spacers/singles/spoutSpacer_airOnly_final_imported_rot_text.dxf
foamboard/front_slim/frontSlimCaptured_v2.dwg
foamboard/front_slim/frontSlimCaptured_v2.dxf
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

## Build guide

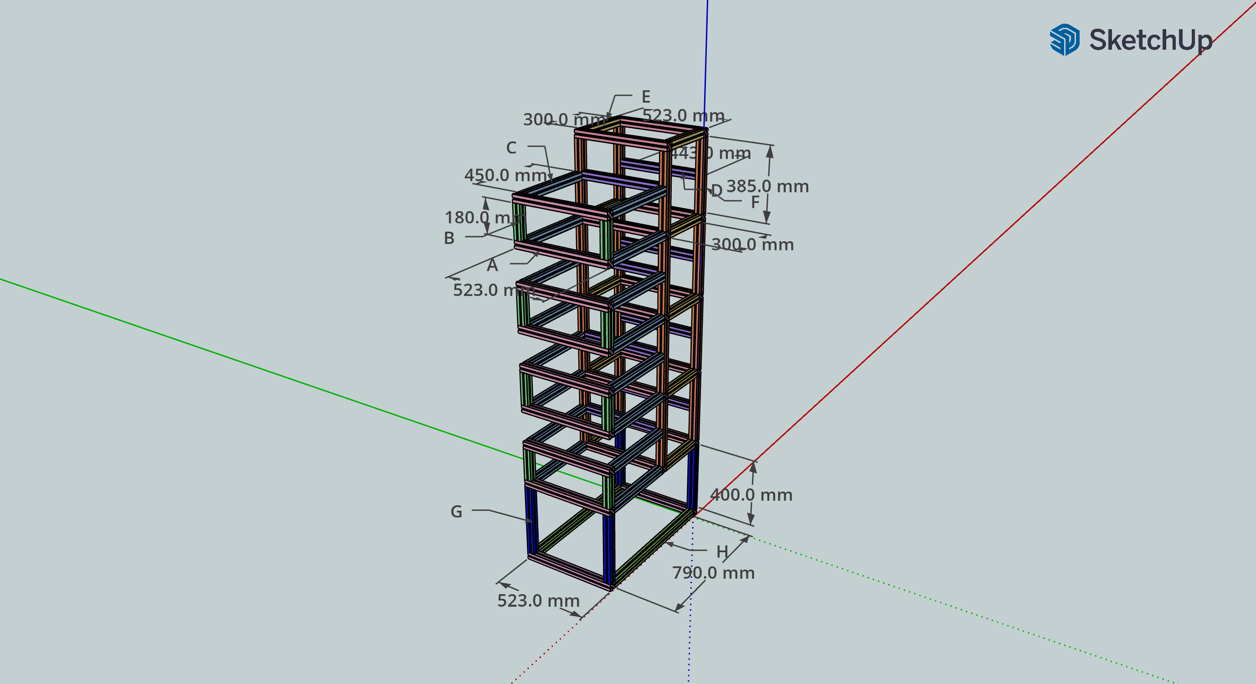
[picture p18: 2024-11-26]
tower_frame/rat_box_assembly.png

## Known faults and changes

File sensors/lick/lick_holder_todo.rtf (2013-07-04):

Acrylic piece for lick-spout holder (notes start with most recent at top):
============================================================================
temporary final pieces:
(1) single spout (under "single" folder) -- v11_imported…etc. file works fine.
(2) triple spout (under "triple" folder) -- .cdr file works fine.

to do:
** would be better to have something more robust (?)
- (Joel): thicker than 0.25" acrylic; threaded luer connectors -- one attaches to tubing, other attaches to stainless steel lick-spout… [some problems though with this]

============================================================================
current file (as of 04.07.2013): lickHolder_v8.dxf/.dxg

**test the following changes:

--new metal-sheet "spade" w/ 90 deg bend, screw down with M3+washer+spade connecting to touch sensor PCB.
--additional third hole added (extending length of spout holder piece), to use 2-hole nut plates to secure spout holder to microrax piece.
--single M2.5 tapped hole now to be put on top (screwing lick spout down, against added piece of sheet metal), rather than having two such holes on sides.
--size of square hole adjusted to fit lick spout + thin sheet metal piece.

============================================================================
file: lickHolder_v6_imported_dxf (1).dxf is most recent / correct version (as of 03.06.2013).

[Added notes, as of 04.03.2013:
--ways to increase surface area of contact between lick-spout itself and hook/wiring from touch sensor…
--currently, Tower2 has 3-sided "bracket" of thin sheet metal, taken from old setups (90 degree bend added by hand), may or may not be worth pursuing more permanent piece]

============================================================================
file: lickHolder_v6_imported_dxf (1).dxf is most recent / correct version (as of 03.06.2013).

--To Do: make sure it actually is…
--previous problems: distance between the 2 thru-holes was too big.
--make sure width of square-hole is good
--**add to "special instructions" :

(1) Need 2 holes perpendicular to square, mid-point. M2.5 screws on both sides of lick tube hold it in place (need both). Mark with pen and *very* carefully and slowly (esp. toward edges) drill through all the way with drill-press. Hand-drilling not good.

** (2) Make sure the correct drill bit is used… should be (I think): 37 (or 39 for close fit) drill bit for the clearance hole, and M2.5x0.45 tap.

============================================================================
** CHANGES on 03.14.2013 -- top edge of holder enlarged (to 0.2050") to test out screwing in M2.5 + metal hook for reward-spout/lick sensor… (length of M2.5 screws = 6mm)

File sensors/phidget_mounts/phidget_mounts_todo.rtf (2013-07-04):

TODO:

1. PHIDGET mount.
(a) unnecessarily wide, taking up space and constraining wiring spacing.
(b) scratch it altogether, and just use the case that Phidget sells… (only for LCD-less one)

2. TOUCH-SENSOR mount.
(a) adjust size or move oval-shaped hole (above each sensor) so that extension-wire can solder onto the back (newer version, off-center) -- this is better than scratching off the plastic backing on the sensors to solder the wire on…
(c) might want to re-arrange horizontal-oval-holes along bottom of mount … for taming the phidget cables.

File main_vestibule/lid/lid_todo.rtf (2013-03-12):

Lid_v14, is the latest version (as of 03.06.2013)

--To Do: move the 4-holes for the computer-mount more medial+anterior, to make room for:
(a) old mac-mini-mount to be turned around, with USB ports facing experimenter, so that monitor adaptor-cables can fit once mounted.
(b) new mac-mini-mount can fit (bigger frame), *also with USB ports facing experimenter

**FINAL version: Lid_v14, as of 03.11.2013.
--change: monitor-mount holes moved, to make room for USB ports and bigger mount.

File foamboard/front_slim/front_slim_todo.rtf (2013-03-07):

frontSlimCaptured_v2 is most recent (as of 03.06.2013)

--To Do: Make sure the cut-outs of bottom have enough "height" to allow for easy through-access for USB, wiring, etc.

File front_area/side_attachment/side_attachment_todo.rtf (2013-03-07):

sideDoorAttachemnt_v3 -- this is actually fine (as of 03.06.2013):

--superficial change would be to remove the 4 corner holes in the attachment piece (along with corresponding tapped-holes in frame piece)
--sufficient to attach with center thumb-screw
--also, can make this piece longer at bottom, to stick into extrusion at bottom.

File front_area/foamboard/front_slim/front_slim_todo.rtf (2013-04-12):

Foam Board piece -- captured, slim area toward monitor end of vestibule (top of setups).
============================================================================
frontSlimCaptured_v4 most recent (as of 04.07.2013):

--version _v3, corners were still too small (adjusted currently to 0.50")

============================================================================
frontSlimCaptured_v2 is most recent (as of 03.06.2013)

--To Do: Make sure the cut-outs of bottom have enough "height" to allow for easy through-access for USB, wiring, etc.

**SET. as of 03.11.2013.

**CHANGE made 03.14.2013 -- 1/4" corners cut out to make room for end-fasteners.

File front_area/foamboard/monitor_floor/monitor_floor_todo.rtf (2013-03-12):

monitorFloor_v3.dxf is the "latest" version (as of 03.06.2013).

--however, the _imported_rot_dxf.dxf file is dated one day earlier -- make sure no essential changes made for the imported file.
--check the printer in machine shop for imported file that might correspond to v3.

**CURRENT VERSION: _v4, should be fixed (as of 03.11.2013).
--problem with _v3 was that the cut-out corners on the 3-hole end were not "deep"/"big" enough, i.e., not enough room for the end-fasteners.
--current version extended cut-out length to 0.75" -- should be okay now

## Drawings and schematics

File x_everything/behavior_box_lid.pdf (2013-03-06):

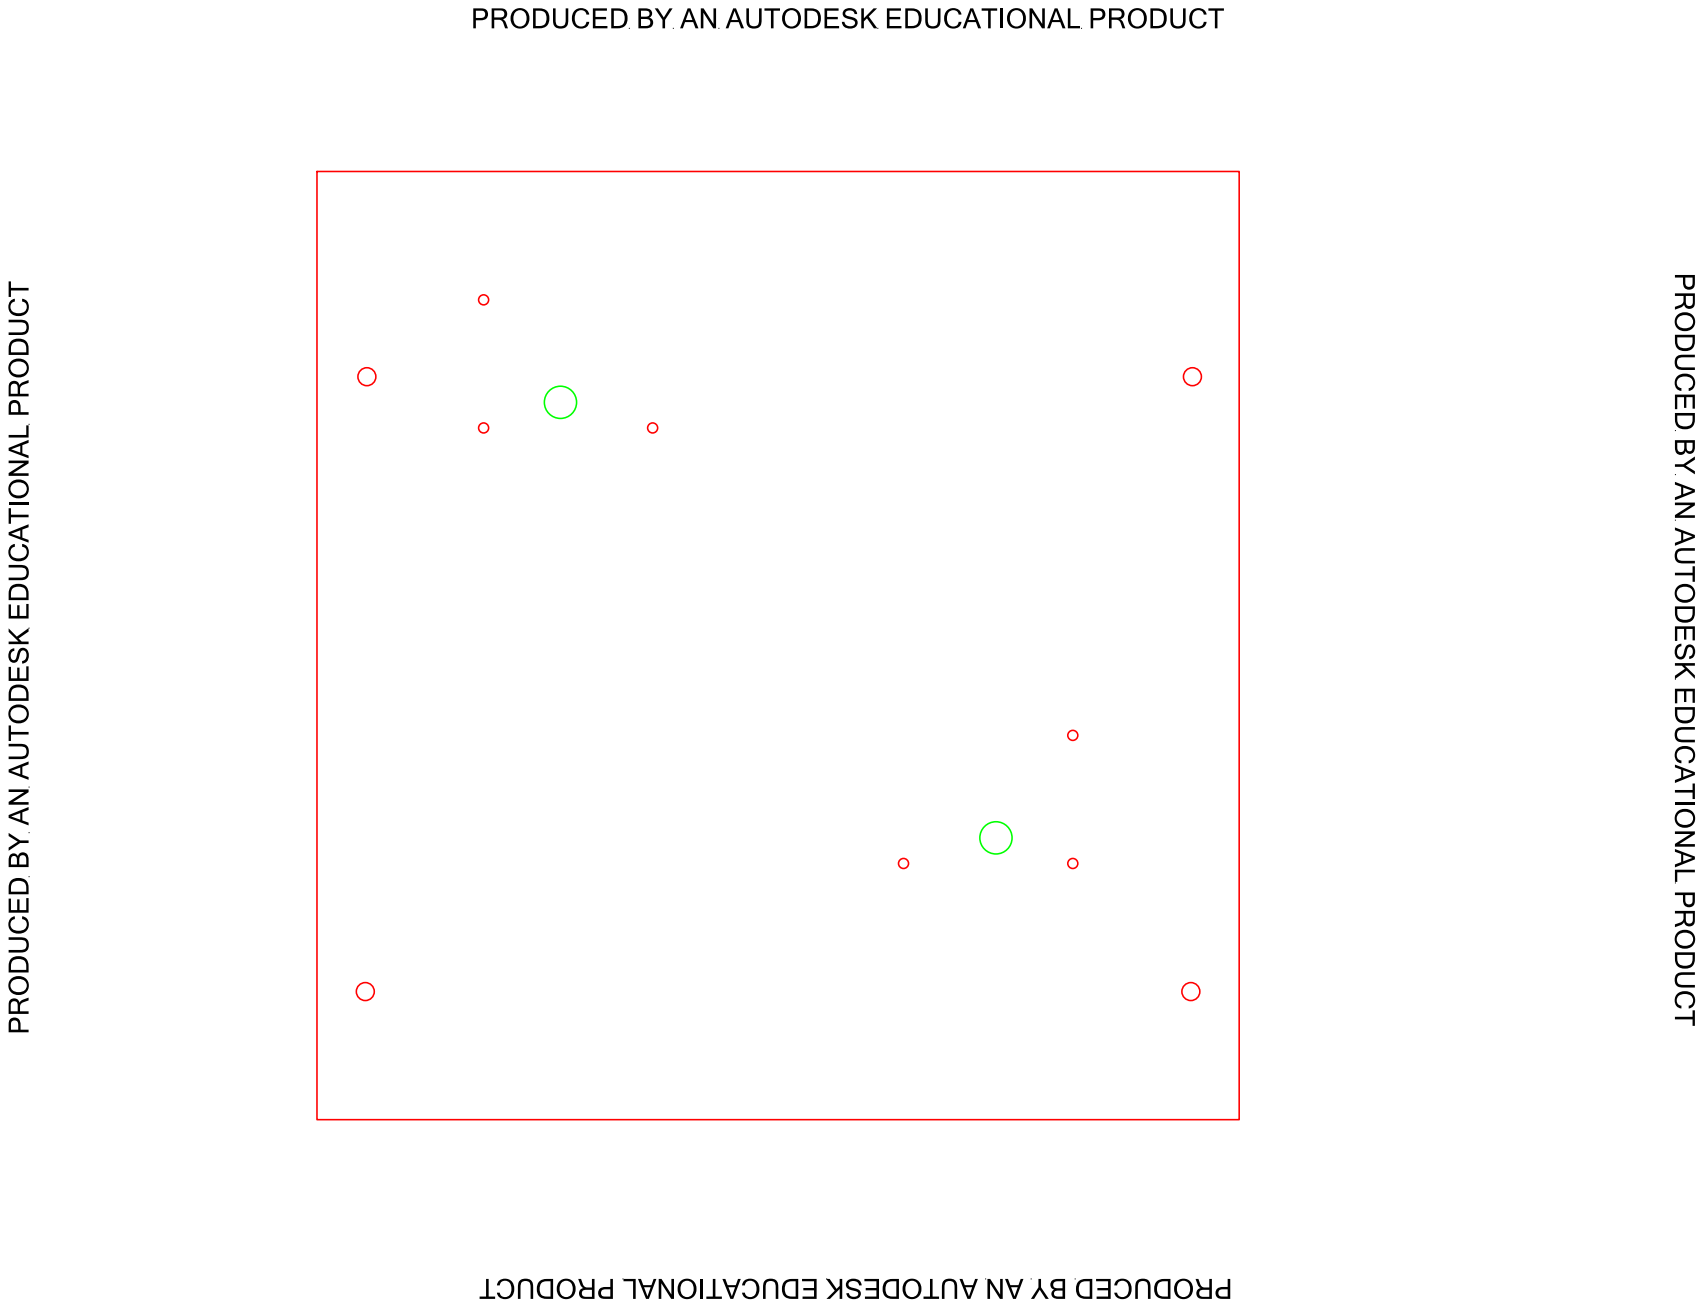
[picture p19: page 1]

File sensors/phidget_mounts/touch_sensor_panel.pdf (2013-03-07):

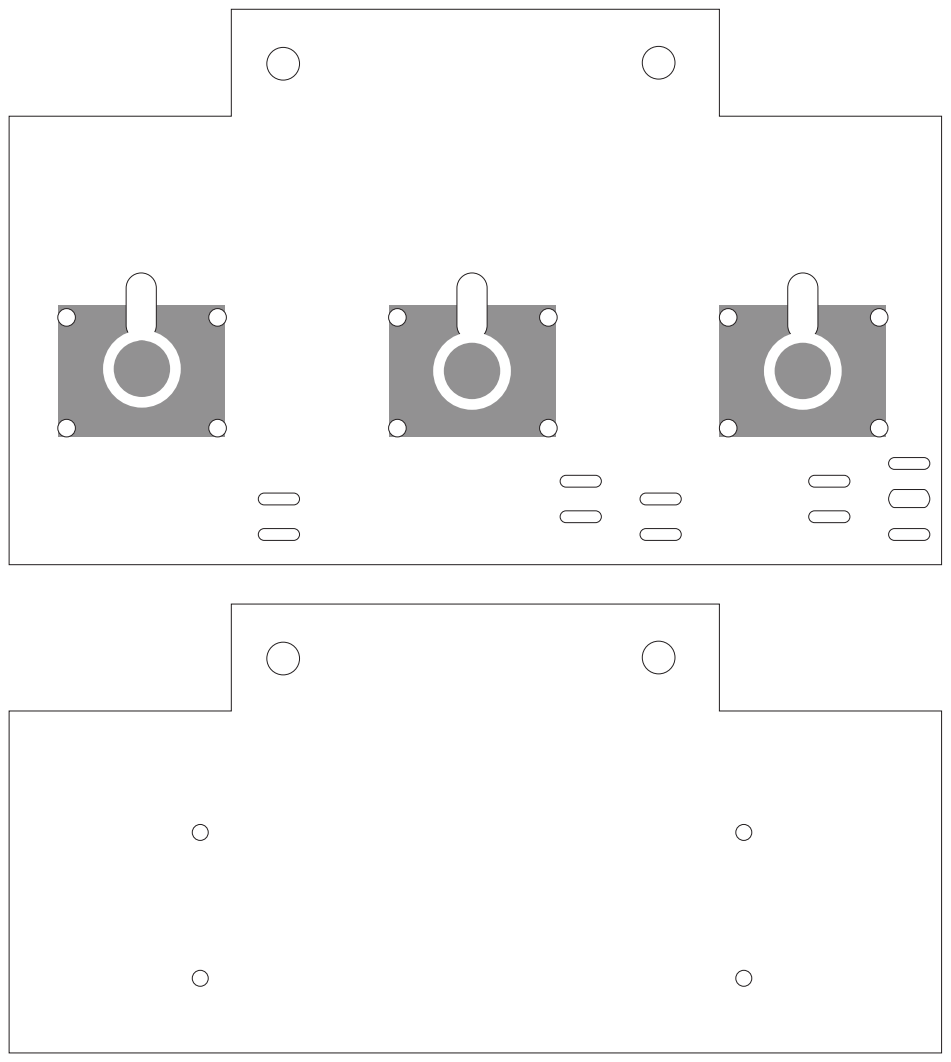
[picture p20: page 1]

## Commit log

2013-03-06 all pieces, all versions, massed into one folder for temp backup
    [Bottom_v1.dwg, Bottom_v1.dxf, Bottom_v1_imported_Rot_Text_dxf.dxf, Bottom_v1b_posteriorShift.dwg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]
2013-03-07 files organized and finalized, exceptions include text file explaining checks or changes to-be-done
    [Bottom_final.dwg, Bottom_final.dxf, Bottom_final_rot_text.dxf, Lid_v14.dwg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]
2013-03-07 re-organized, plus phidget- and sensor-mounts added
    [sideCaptured_final.dwg, sideCaptured_final.dxf, sideCaptured_final_imp.dxf, sidePanel_final.dwg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]
2013-03-12 slight changes made to finalized versions, especially, acrylic lid and bottom pieces, and foamboard monitor-floor and rack-top pieces
    [Bottom_final.dwg, Bottom_final.dxf, Bottom_final_rot_text.dxf, Bottom_v5.dwg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]
2013-03-15 foamboard front-slim piece, corner cut-outs added; lick-holder acrylic piece, top dimension slightly enlarged to test for screwing in lick-spout from top rather than sides
    [Bottom_v5_imported_rot_text_dxf.dxf, frontSlimCaptured_v2.dwg, frontSlimCaptured_v2.dxf, frontSlimCaptured_v2_imported_rot.dxf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]
2013-03-15 Adding sketchup files for the 80-20 frame
    [rat_box.skp]
2013-03-16 Add assembly and update BOM
    [rat_box_assembly.skp]
2013-03-16 remaining finalized pieces added
    [doorHinge_final.dwg, doorHinge_final.dxf, doorHinge_final_adjusted.dxf, doorHinge_final_rot.dxf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]
2013-03-17 added tower-frame folder
    [rat_box.skp, rat_box_assembly.skp]
2013-03-22 calibration notes for touchscreen monitor supplemented
2013-04-04 in-progress excel spreadsheet specifying acrylic and accessory parts, plus in-progress special assembly notes
    [behav_rig_specs_v2.xlsx]
2013-04-12 some changes to lickHolder piece, plus additional changes in preparation for final acrylic order to complete 4 towers
    [acrylic_b3_v2.dwg, behav_rig_specs_final.xlsx, doorHinge_final.dwg, frontSlimCaptured_v3.dwg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]
2013-04-16 additional changes, especially to front-area pieces, as well as addition of finalized pieces, relative to acrylic order from 04.15.2013
    [behav_rig_specs_final.xlsx, frontSlimCaptured_v4_imported_rot_dxf.dxf, lickHolder_v9.dwg, lickHolder_v9.dxf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]
2013-04-25 adjusted captured acrylic pieces for side_frame and both attachments, slotted and door
    [behav_rig_specs_final.xlsx, sideDoorAttachment_short.dwg, sideDoorAttachment_v5.dwg, sideDoorFrame_v4.dwg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]
2013-04-30 final side_frame piece, plus newest single-spout holder and triple-spout holder pieces
    [door_final_text.dxf, lickHolder_three_v1.dwg, lickHolder_three_v1.dxf, lickHolder_v10.dwg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]
2013-05-02 Moved old files away
    [monitorMount_v3_big.dwg, monitorMount_v3_big.dxf]
2013-05-07 changes to lickHolder design, single and triples added'
    [lickHolder_three_v1.dwg, lickHolder_v10.dwg, lickHolder_v10.dxf, lickHolder_v11.dwg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]
2013-05-07 organized into single vs triple sensor holders
    [lickHolder_three_v1.dwg, lickHolder_three_v1.dxf, lickHolder_v11.dwg, lickHolder_v11.dxf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]
2013-05-07 draft of new monitor mount, for larger mount spacings to attach to extrusion bar
    [monitorMount_new_v1.dwg]
2013-05-07 removing misnamed files that occurred while moving files into new folders
    [lickHolder_v6_imported_dxf (1).dwg]
2013-05-12 wider monitor mount for new monitors, samsung 943BT model
    [monitorMount_final.dwg, monitorMount_final.dxf, monitorMount_final_rot.dxf, monitorMount_small_extended.dwg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]
2013-05-12 updated changes to monitor mount, outlines which monitor goes with which mount
2013-05-12 most recent changes to reward spout holders, single and triple, triple's spacing adjusted to better match old-setup lick trays
    [lickHolder_three_v1.dwg, lickHolder_v11.dwg]
2013-05-29 small adjustments made to new side-door-window design, and also foam pieces
    [frontSlimCaptured_v4.dxf, frontSlimCaptured_v4_imported_rot_dxf.dxf, rackTop_final_imported_rot.dxf, sideDoorAttachment_short_imported_dxf.dxf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]
2013-05-29 most recent and/or finalized pieces udpated and reorganized
    [frontSlimCaptured_v2.dwg, frontSlimCaptured_v2.dxf, frontSlimCaptured_v2_imported_rot.dxf, monitorFloor_imported_rot_dxf.dxf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]
2013-05-29 slightly bigger holes for M3s and MicroRax frame in front, to account for slight differences in 90-deg brackets from MicroRax
    [Bottom_v6.dwg, Bottom_v6.dxf]
2013-05-29 side frame and attachment pieces udpated, finalized, confirmed, with corresponding notes and folder setup
    [sideDoorAttachment_v3.dwg, sideDoorAttachment_v3.dxf, sideDoorAttachment_v3_imported_dxf.dxf, sideDoorAttachment_v5.dwg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]
2013-05-29 old and/or misplaced files cleared away
    [Lid_v14.dwg, Lid_v14.dxf, Lid_v15_imported_rot_text_dxf.dxf, sideCaptured_final.dwg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]
2013-05-29 just need the file for all spacers, 3x, to fit in pre-cut acrylic piece (see spreadsheet notes, if nec)
    [spoutSpacer_H2Oonly_final.dwg, spoutSpacer_H2Oonly_final.dxf, spoutSpacer_H2Oonly_final_imported_text.dxf, spoutSpacer_airOnly_final.dwg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]
2013-07-04 updating finalized pieces, plus adding notes to particlar pieces (see text files, when relevant)
    [Bottom_final.dwg, Bottom_final.dxf, Bottom_final_rot_text.dxf, Bottom_v5_imported_rot_textdxf.dxf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]
2015-06-12 Added power_squid_mount.pdf and its readme.
2015-06-18 unadded changes to commit
    [Bottom_final.dwg, Bottom_final.dxf, Bottom_final_rot_text.dxf, Bottom_v1.dwg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]
2024-11-26 adding detailed readme. updated construction notes. added helpful images
    [behav_rig_specs_final.xlsx]
